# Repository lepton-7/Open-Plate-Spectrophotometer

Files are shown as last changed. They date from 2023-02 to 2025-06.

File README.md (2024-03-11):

# Open-Plate-Spectrophotometer

An open-source project to build a 96-well spectrophotometer operating at 620nm. Designed from the ground-up focusing on robust electronic design. Funded by the [think[box] Student Project Fund](https://case.edu/thinkbox/funding/student-project-fund) for the 2022-2023 academic year.

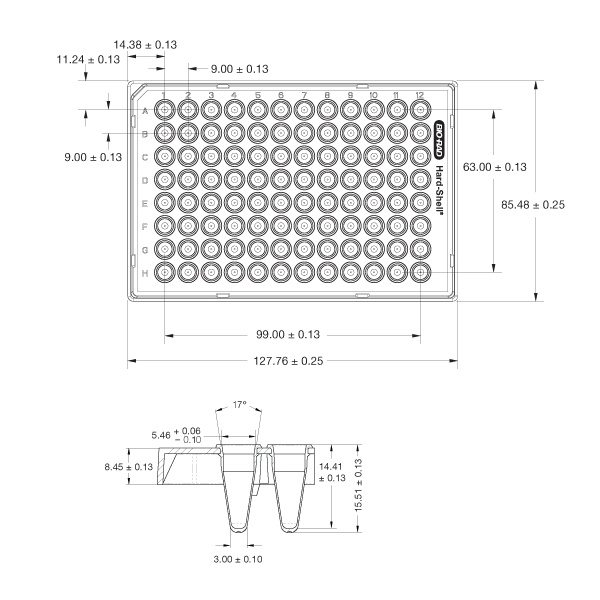
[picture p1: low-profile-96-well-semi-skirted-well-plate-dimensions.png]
plate


## Test Prototype (v0.0.2)

This project was born out of an appreciation for [Cerillo's portable microplate reader](https://cerillo.bio/stratus-2/) and the arrogant desire to open-source it by recreating what they made on my own. I designed a limited test prototype during the summer (I think sometime in July?) before the school year restarted to see what is required to realise the idea of a small form-factor, portable plate reader.

### Concept and Schematic

#### Functional block diagram

Functional block diagram

The idea is simple: control 96-element grids of LEDs and light sensors to address individual wells in a plate, convert the signal from the light sensor into something machine parsable, then finally do some ✨math✨ to get an optical density value for each well.

#### LED and detector grids

I decided to _not_ build a full 96-capable prototype. Instead, I opted to test all the relevant units I needed on a smaller scale. The result was a prototype with all 8 rows (A-H) but only two columns.

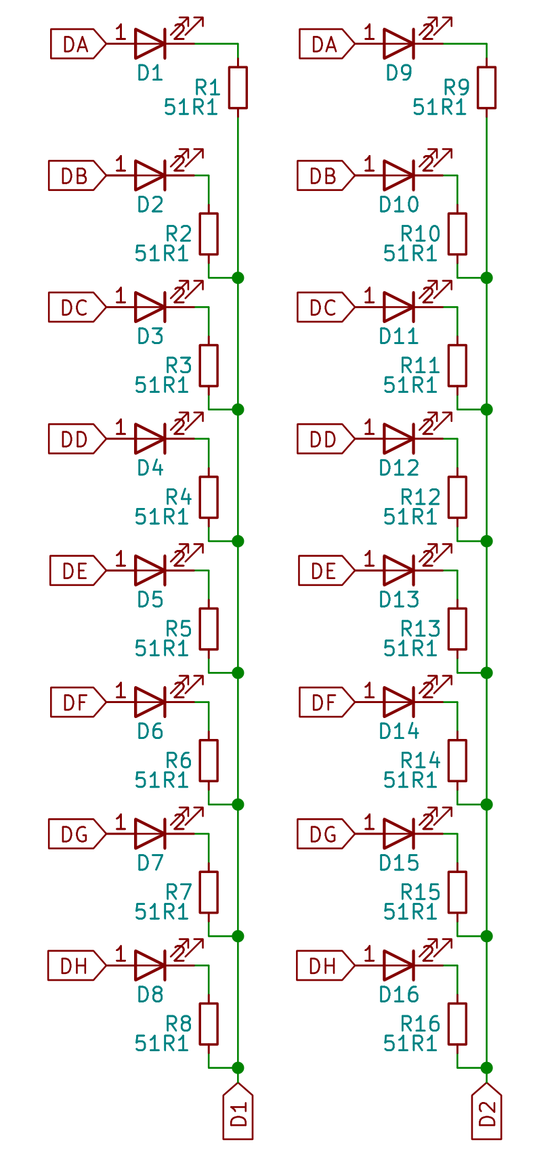
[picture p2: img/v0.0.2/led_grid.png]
led grid

Independent control of each element is easily achieved by connecting the grid high and low sides to control MOSFETs:

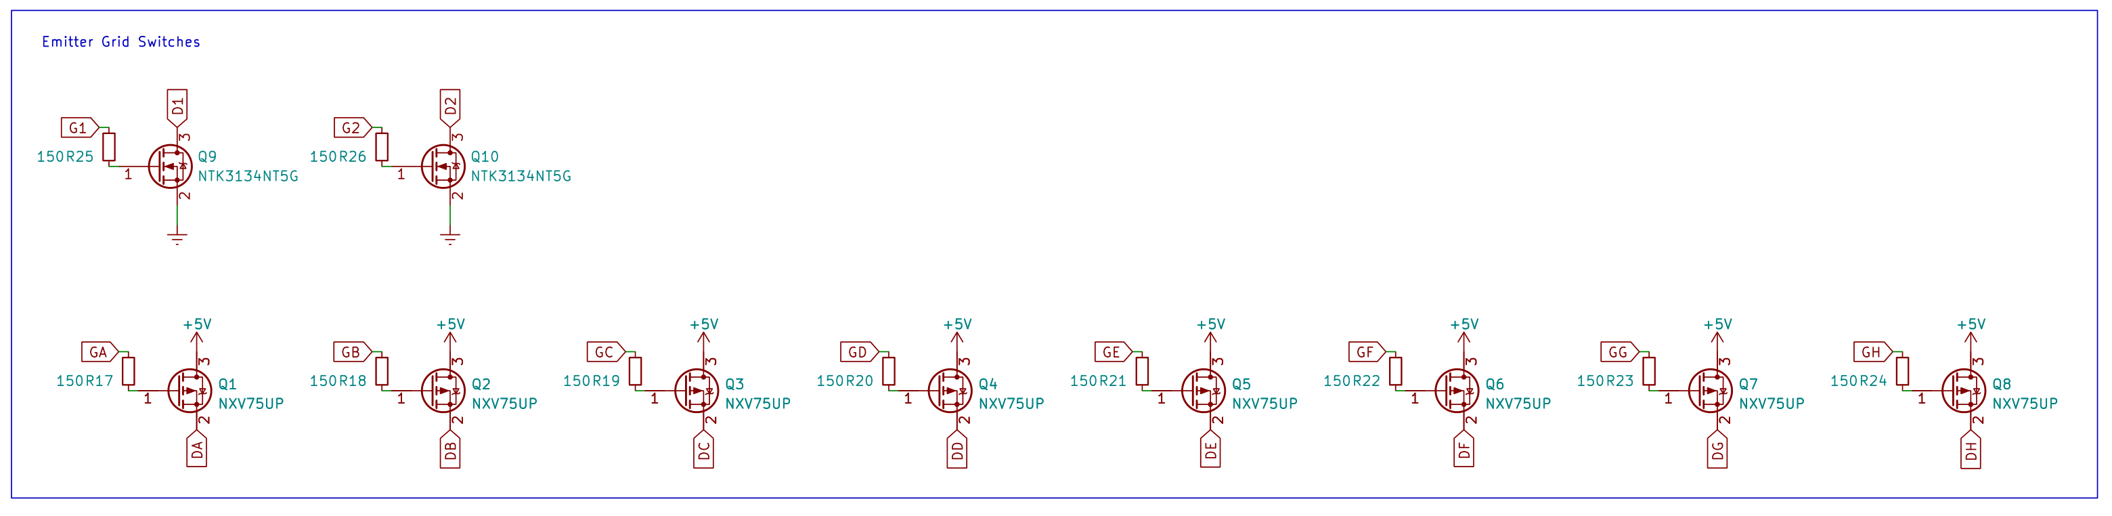
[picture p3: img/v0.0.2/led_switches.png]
led switches

Each row was connected to +5V via p-ch FETs (yes i know, they're wired incorrectly) and each column was connected to GND via n-ch FETs. Each FET gate is assigned its own pin on the MCU to independently control individual elements.

A similar idea is used for switching inputs from specific photodiode elements.

#### Detectors: photodiodes vs phototransistors

The hard bit for a device like this taking light that passes through the sample wells and converting that into a digital signal. Initially, I planned on using [phototransistors](https://www.digikey.com/en/articles/the-basics-of-photodiodes-and-phototransistors-and-how-to-apply-them) to transform a change in incident light intensity into a change in current. But these devices are pretty imprecise and do not have the best linearity. To make phototransistors work, I would have needed to do some really careful biasing -- something I did not think I needed.

The alternative was to use photodiodes. These are a bit better in the sense that they would have required a lot fewer supporting components. They also have pretty nice characteristics:

<fig>
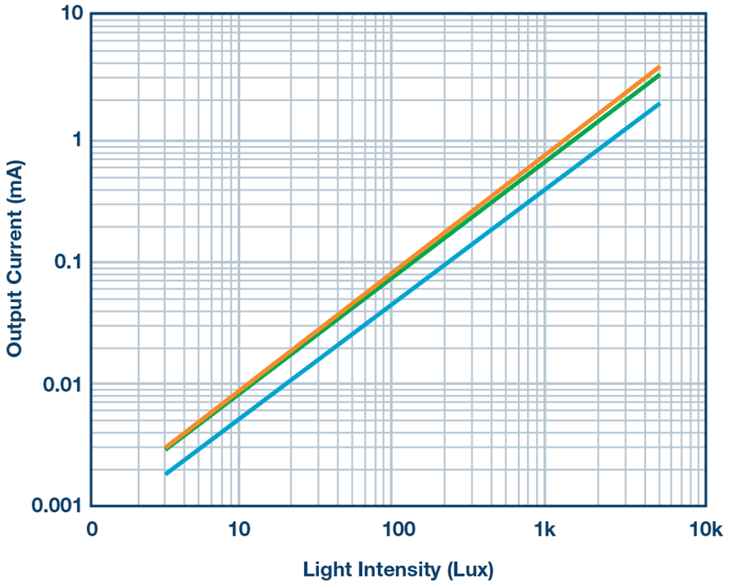
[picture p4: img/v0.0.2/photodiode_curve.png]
photodiode curve

<figcaption>Plot from Analog ADI</figcaption>
</fig>

These devices are pretty much linear in their response to incident light intensity: A 10x increase in incident intensity results in a 10x increase in reverse current.

#### Transimpedance amplifiers and ADCs

Converting current going through a photodiode into digital information is a two-step process. This is nothing new; the typical strategy is to use a transimpedance amplifier to convert transform a current signal into a voltage signal followed by an ADC that can convert the voltage signal into a digital value:

<fig>
TIA
<figcaption>TIA diagram from wikimedia commons.</figcaption>
</fig>

The transfer function is also pretty simple for a TIA:
$$ V_{out} = -I_{in}R_f $$

This is implemented as:

<fig>
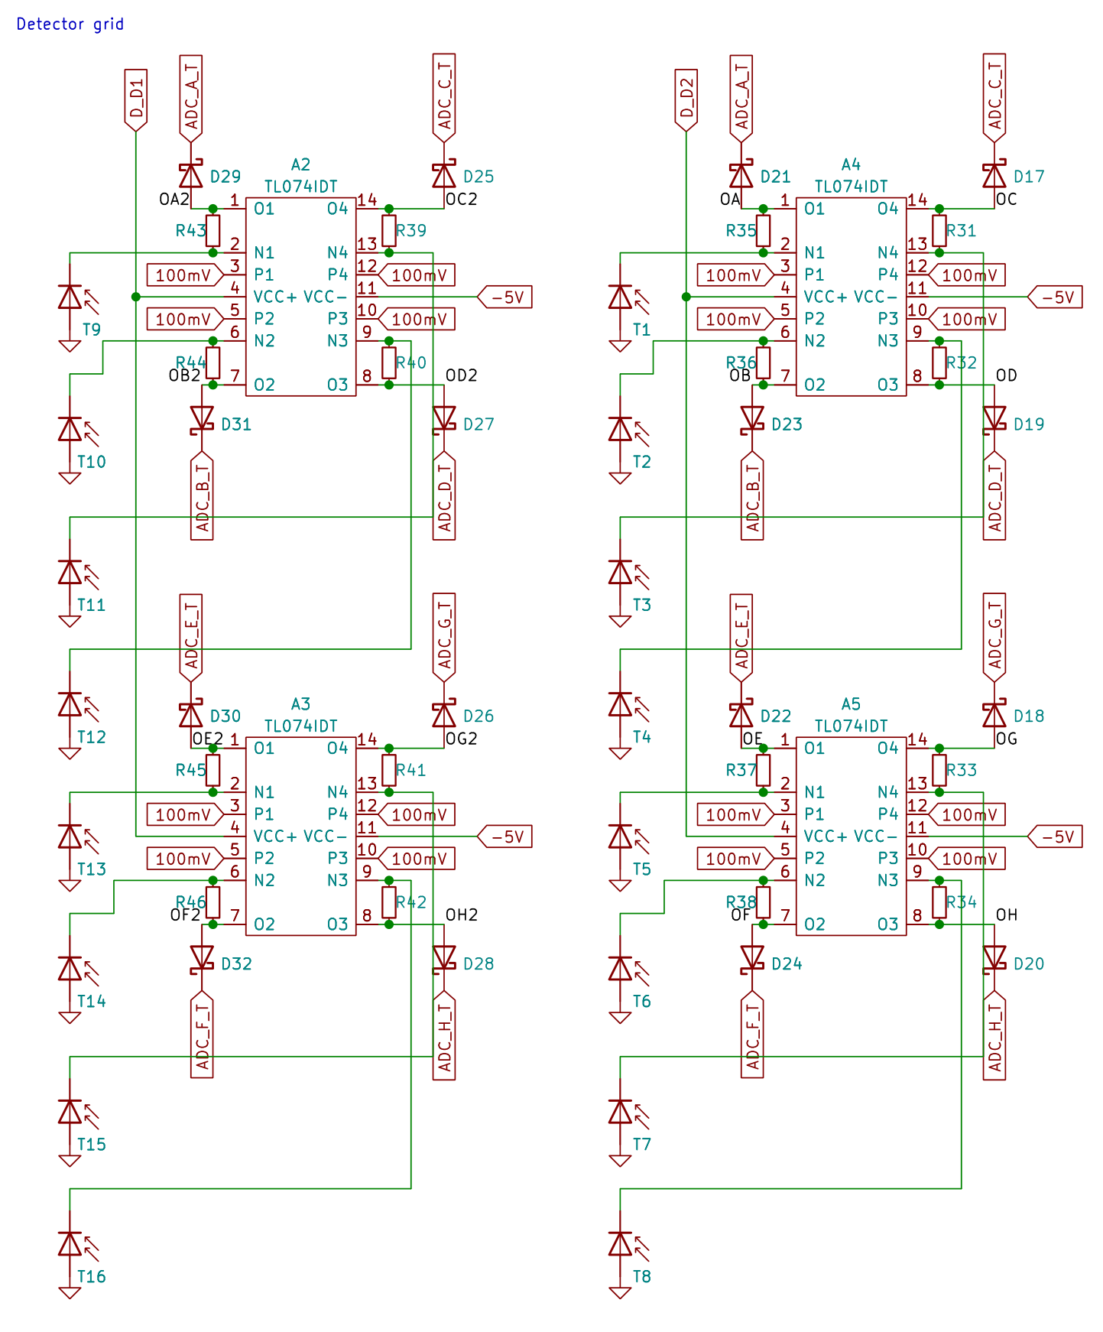
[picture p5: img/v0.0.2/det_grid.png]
photodiode grid

</fig>

The principle is the same, just compressed a little. The current source is replaced by the photodiode, mulit-channel opamps are used to save space, and $V_{out}$ passes through a standard Schottky diode before being connected to the ADC inputs.

I used an 8ch ADC to independently connect each row for pseudo-switching of the detector outputs. High-side p-ch FET switches control V<sub>cc</sub> for the TIAs.

<fig>
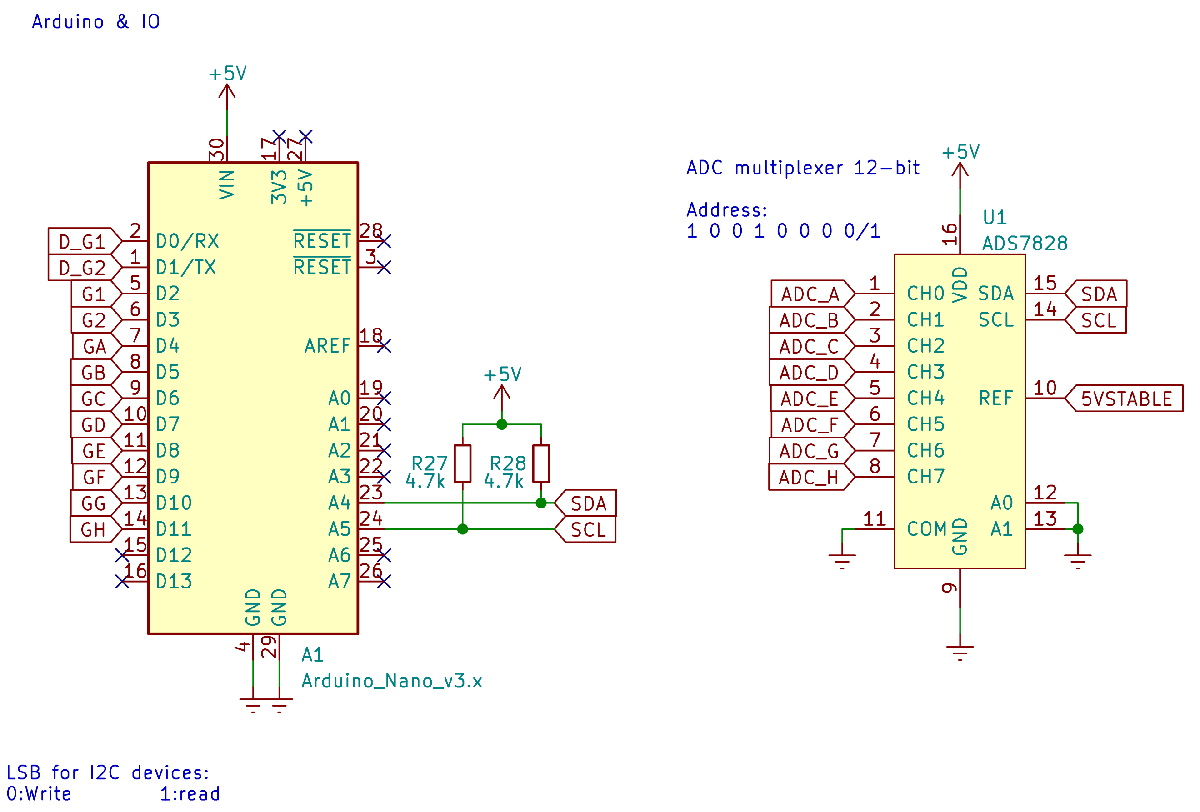
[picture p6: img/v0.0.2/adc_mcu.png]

</fig>

The 12-bit ADC converts output voltage into a digital signal referenced to a stable 5V signal generated by a voltage reference amplified by a low-noise voltage follower:

<fig>
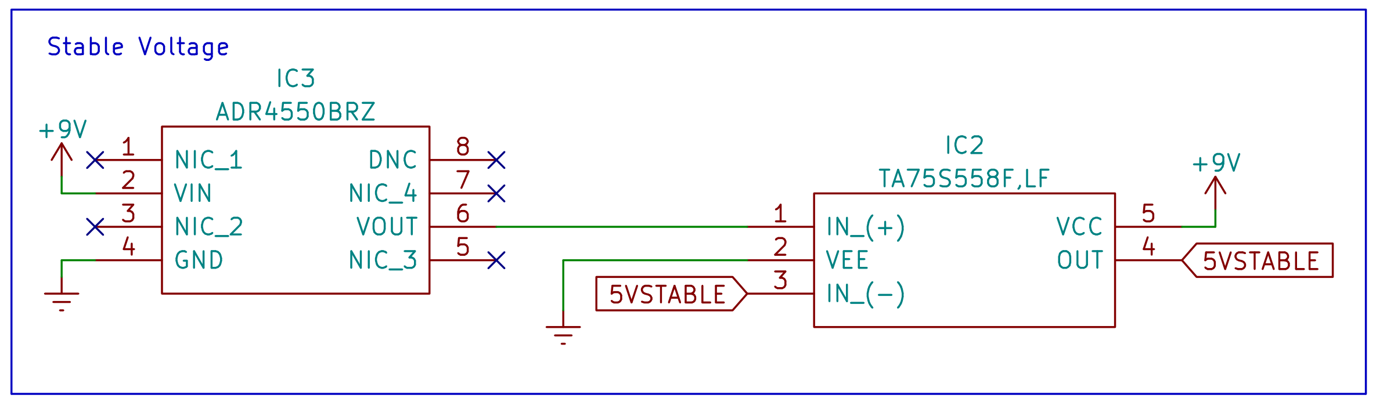
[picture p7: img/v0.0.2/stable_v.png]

</fig>

The MCU, an arduino nano, communicates with the ADC over I<sup>2</sup>C.

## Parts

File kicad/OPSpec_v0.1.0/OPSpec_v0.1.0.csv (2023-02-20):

Source: | C:\School stuff\Bagby Lab\Projects\OPSpec\kicad\OPSpec_v0.1.0\OPSpec_v0.1.0.kicad_sch
Date: | 25/11/2022 14:10
Tool: | Eeschema (6.0.5)
Generator: | C:\Program Files\KiCad\6.0\bin\scripting\plugins/bom_csv_grouped_by_value.py
Component Count: | 661
Collated Components:
Item | Qty | Reference(s) | Value | LibPart | Footprint | Datasheet | Description | Height | Manufacturer_Name | Manufacturer_Part_Number | Mouser Part Number | Mouser Price/Stock
1 | 101 | C1, C2, C3, C4, C5, C6, C7, C8, C9, C10, C11, C12, C13, C14, C15, C16, C17, C18, C19, C20, C21, C22, C23, C24, C25, C26, C27, C28, C29, C30, C31, C32, C33, C34, C35, C36, C37, C38, C39, C40, C41, C42, C43, C44, C45, C46, C47, C48, C49, C50, C51, C52, C53, C54, C55, C56, C57, C58, C59, C60, C61, C62, C63, C64, C65, C66, C67, C68, C69, C70, C71, C72, C73, C74, C75, C76, C77, C78, C79, C80, C81, C82, C83, C84, C85, C86, C87, C88, C89, C90, C91, C92, C93, C94, C95, C96, C98, C100, C105, C154, C174 | 1u | Device:C_Small | Capacitor_SMD:C_0603_1608Metric | ~
2 | 40 | C97, C99, C103, C106, C107, C108, C109, C110, C111, C112, C113, C114, C115, C116, C117, C118, C119, C120, C121, C122, C131, C132, C133, C134, C135, C136, C137, C138, C149, C151, C155, C156, C158, C161, C163, C164, C167, C169, C171, C173 | 100nF | Device:C_Small | Capacitor_SMD:C_0603_1608Metric | ~
3 | 10 | C101, C102, C104, C150, C152, C157, C160, C166, C168, C172 | 10uF | Device:C_Small | Capacitor_SMD:C_0805_2012Metric | ~
4 | 16 | C123, C124, C125, C126, C127, C128, C129, C130, C139, C140, C141, C142, C143, C144, C145, C146 | 100pF | Device:C_Small | Capacitor_SMD:C_0603_1608Metric | ~
5 | 6 | C147, C148, C159, C162, C165, C170 | 470nF | Device:C_Small | Capacitor_SMD:C_0805_2012Metric | ~
6 | 1 | C153 | 470pF | Device:C_Small | Capacitor_SMD:C_0603_1608Metric | ~
7 | 96 | D1, D2, D3, D4, D5, D6, D7, D8, D9, D10, D11, D12, D13, D14, D15, D16, D17, D18, D19, D20, D21, D22, D23, D24, D25, D26, D27, D28, D29, D30, D31, D32, D33, D34, D35, D36, D37, D38, D39, D40, D41, D42, D43, D44, D45, D46, D47, D48, D49, D50, D51, D52, D53, D54, D55, D56, D57, D58, D59, D60, D61, D62, D63, D64, D65, D66, D67, D68, D69, D70, D71, D72, D73, D74, D75, D76, D77, D78, D79, D80, D81, D82, D83, D84, D85, D86, D87, D88, D89, D90, D91, D92, D93, D94, D95, D96 | GR_JTLPS1.23-G7H4-45-1-150-R33 | LED:GR_JTLPS1.23-G7H4-45-1-150-R33 | SamacSys_Parts:GRJTLPS123G7H4451150R33 | ~ | High Power LEDs - Single Color Red DURIS E 2835 | 0.8 | OSRAM | GR JTLPS1.23-G7H4-45-1-150-R33 | 720-GRJTLPS123A1052 | https://www.mouser.co.uk/ProductDetail/OSRAM-Opto-Semiconductors/GR-JTLPS123-G7H4-45-1-150-R33?qs=T94vaHKWudSzDFhf8Pfs5w%3D%3D
8 | 8 | H1, H2, H3, H4, H5, H6, H7, H8 | MountingHole | Mechanical:MountingHole_Pad | MountingHole:MountingHole_4.3mm_M4_Pad | ~
9 | 3 | IC1, IC2, IC7 | PCA9555APW,118 | Interface_Expansion:PCA9555APW,118 | SamacSys_Parts:SOP65P640X110-24N | http://www.nxp.com/docs/en/data-sheet/PCA9555A.pdf | NXP - PCA9555APW,118 - I/O EXPANDER, 16BIT, 400KHZ, TSSOP-24 | 1.1 | NXP | PCA9555APW,118 | 771-PCA9555APW118 | https://www.mouser.co.uk/ProductDetail/NXP-Semiconductors/PCA9555APW118?qs=5C9Q4QJFsuPmpoGpn%2FKoIQ%3D%3D
10 | 1 | IC3 | MCP1801T-6002I_OT | SamacSys_Parts:MCP1801T-6002I_OT | SamacSys_Parts:SOT95P270X145-5N | https://www.mouser.in/datasheet/2/268/22051D-474537.pdf | LDO Voltage Regulators Hi PSRR 150 mA LDO Vin 10V maxVout 6.0V | 1.45 | Microchip | MCP1801T-6002I/OT | 579-MCP1801T-6002IOT | https://www.mouser.co.uk/ProductDetail/Microchip-Technology/MCP1801T-6002I-OT?qs=aE5D7Pt6ky2EwNge7jBPcQ%3D%3D
11 | 3 | IC4, IC5, IC6 | TAR5S50TE85LF | Regulator_Linear:TAR5S50TE85LF | SamacSys_Parts:SMV_1 | https://toshiba.semicon-storage.com/info/docget.jsp?did=766&prodName=TAR5S40 | LDO Voltage Regulators Point Reg SGL output 200mA 15V 5V out |  | Toshiba | TAR5S50TE85LF | 757-TAR5S50TE85LF | https://www.mouser.co.uk/ProductDetail/Toshiba/TAR5S50TE85LF?qs=lQAVKuKFhkISS%252B6HLQK7hg%3D%3D
12 | 1 | J1 | BASE_INTERFACE | :Conn_01x14_Female_1 | Connector_FFC-FPC:TE_1-1734839-4_1x14-1MP_P0.5mm_Horizontal | ~
13 | 1 | J2 | 163-179PH-EX | Connector:Barrel_Jack_Switch | Connector_BarrelJack:BarrelJack_Wuerth_6941xx301002 | ~
14 | 1 | J3 | Arduino | Connector:Conn_01x04_Male | Connector_PinHeader_2.54mm:PinHeader_1x04_P2.54mm_Vertical | ~
15 | 1 | J4 | TOP_INTERFACE | Connector:Conn_01x14_Female | Connector_FFC-FPC:TE_1-1734839-4_1x14-1MP_P0.5mm_Horizontal | ~
16 | 1 | L1 | 3.3uH | SamacSys_Parts:MAKK2016T3R3M | SamacSys_Parts:INDPM2016X100N |  | Fixed Inductors 0806 3.3uH 255mOhms +/-20% 1150A HiCur | 1 | TAIYO YUDEN | MAKK2016T3R3M | 963-MAKK2016T3R3M | https://www.mouser.co.uk/ProductDetail/Taiyo-Yuden/MAKK2016T3R3M?qs=Z6svWd%2FY2UTQY1%2FASu%252BfUw%3D%3D
17 | 8 | LA1, LA2, LA3, LA4, LA5, LA6, LA7, LA8 | MAX4206ETE+T | Amplifier_Operational:MAX4206ETE+T | SamacSys_Parts:QFN65P400X400X80-17N | https://datasheets.maximintegrated.com/en/ds/MAX4206.pdf | Logarithmic Amplifiers Precision Transimpedance Logarithmic Amplifier with Over 5 Decades of Dynamic Range | 0.8 | Maxim Integrated | MAX4206ETE+T | 700-MAX4206ETE+T | https://www.mouser.co.uk/ProductDetail/Maxim-Integrated/MAX4206ETE%2bT?qs=1eQvB6Dk1vihFrrDtkPdrA%3D%3D
18 | 12 | Q1, Q2, Q3, Q4, Q5, Q6, Q7, Q8, Q9, Q10, Q11, Q12 | NTK3134NT5G | Device:Q_NMOS_GSD | SamacSys_Parts:NTK3134NT5G | https://www.onsemi.com/pdf/datasheet/ntk3134n-d.pdf | N-Channel 20 V 750mA (Ta) 310mW (Ta) Surface Mount SOT-723 | 0.55 | onsemi | NTK3134NT5G | 863-NTK3134NT5G | https://www.mouser.co.uk/ProductDetail/onsemi/NTK3134NT5G?qs=g97OBWmz8%2FWdltr4eSy1YA%3D%3D
19 | 20 | Q13, Q14, Q15, Q16, Q17, Q18, Q19, Q20, Q21, Q22, Q23, Q24, Q25, Q26, Q27, Q28, Q29, Q30, Q31, Q32 | NXV75UP | Device:Q_PMOS_GSD | Package_TO_SOT_SMD:SOT-23 | ~
20 | 6 | Q33, Q34, Q35, Q36, Q37, Q38 | 2SCR502UBTL | Transistor_BJT:2SCR502UBTL | SamacSys_Parts:SOTFL65P210X105-3N | https://componentsearchengine.com/Datasheets/1/2SCR502UBTL.pdf | Signal Transistor NPN 30V 500mA UMT3F | 1.05 | ROHM Semiconductor | 2SCR502UBTL | 755-2SCR502UBTL | https://www.mouser.com/Search/Refine.aspx?Keyword=755-2SCR502UBTL
21 | 96 | R1, R2, R3, R4, R5, R6, R7, R8, R9, R10, R11, R12, R13, R14, R15, R16, R17, R18, R19, R20, R21, R22, R23, R24, R25, R26, R27, R28, R29, R30, R31, R32, R33, R34, R35, R36, R37, R38, R39, R40, R41, R42, R43, R44, R45, R46, R47, R48, R49, R50, R51, R52, R53, R54, R55, R56, R57, R58, R59, R60, R61, R62, R63, R64, R65, R66, R67, R68, R69, R70, R71, R72, R73, R74, R75, R76, R77, R78, R79, R80, R81, R82, R83, R84, R85, R86, R87, R88, R89, R90, R91, R92, R93, R94, R95, R96 | 51R1 | Device:R_Small | Resistor_SMD:R_0603_1608Metric | ~
22 | 32 | R97, R99, R101, R103, R105, R107, R109, R111, R113, R115, R117, R119, R129, R130, R131, R132, R133, R134, R135, R136, R142, R144, R146, R148, R150, R152, R154, R156, R158, R160, R162, R164 | 100k | Device:R_Small | Resistor_SMD:R_0603_1608Metric | ~
23 | 32 | R98, R100, R102, R104, R106, R108, R110, R112, R114, R116, R118, R120, R121, R122, R123, R124, R125, R126, R127, R128, R141, R143, R145, R147, R149, R151, R153, R155, R157, R159, R161, R163 | 150 | Device:R_Small | Resistor_SMD:R_0603_1608Metric | ~
24 | 27 | R137, R138, R173, R174, R175, R176, R177, R178, R179, R180, R211, R212, R213, R214, R215, R216, R217, R218, R219, R220, R221, R222, R223, R224, R225, R226, R227 | 10k | Device:R_Small | Resistor_SMD:R_0603_1608Metric | ~
25 | 2 | R139, R140 | 4.7k | Device:R_Small | Resistor_SMD:R_0603_1608Metric | ~
26 | 8 | R165, R166, R167, R168, R169, R170, R171, R172 | 38k3 | Device:R_Small | Resistor_SMD:R_0603_1608Metric | ~
27 | 8 | R181, R182, R183, R184, R185, R186, R187, R188 | 499k | Device:R_Small | Resistor_SMD:R_0603_1608Metric | ~
28 | 16 | R189, R190, R191, R192, R193, R194, R195, R196, R197, R198, R199, R200, R201, R202, R203, R204 | 100 | Device:R_Small | Resistor_SMD:R_0603_1608Metric | ~
29 | 6 | R205, R206, R207, R208, R209, R210 | 511 | Device:R_Small | Resistor_SMD:R_0603_1608Metric | ~
30 | 96 | T1, T2, T3, T4, T5, T6, T7, T8, T9, T10, T11, T12, T13, T14, T15, T16, T17, T18, T19, T20, T21, T22, T23, T24, T25, T26, T27, T28, T29, T30, T31, T32, T33, T34, T35, T36, T37, T38, T39, T40, T41, T42, T43, T44, T45, T46, T47, T48, T49, T50, T51, T52, T53, T54, T55, T56, T57, T58, T59, T60, T61, T62, T63, T64, T65, T66, T67, T68, T69, T70, T71, T72, T73, T74, T75, T76, T77, T78, T79, T80, T81, T82, T83, T84, T85, T86, T87, T88, T89, T90, T91, T92, T93, T94, T95, T96 | S16392-01CT | Device:D_Photo | Diode_SMD:S16392-01CT | ~
31 | 1 | U1 | AP63205WU | Regulator_Switching:AP63205WU | Package_TO_SOT_SMD:TSOT-23-6 | https://www.diodes.com/assets/Datasheets/AP63200-AP63201-AP63203-AP63205.pdf
32 | 1 | U2 | ADS7828 | Analog_ADC:ADS7828 | Package_SO:TSSOP-16_4.4x5mm_P0.65mm | http://www.ti.com/lit/ds/symlink/ads7828.pdf
Individual Components:
Item | Qty | Reference(s) | Value | LibPart | Footprint | Datasheet | Description | Height | Manufacturer_Name | Manufacturer_Part_Number | Mouser Part Number | Mouser Price/Stock
 |  | C1 | 1u | Device:C_Small | Capacitor_SMD:C_0603_1608Metric | ~
 |  | C2 | 1u | Device:C_Small | Capacitor_SMD:C_0603_1608Metric | ~
 |  | C3 | 1u | Device:C_Small | Capacitor_SMD:C_0603_1608Metric | ~
 |  | C4 | 1u | Device:C_Small | Capacitor_SMD:C_0603_1608Metric | ~
 |  | C5 | 1u | Device:C_Small | Capacitor_SMD:C_0603_1608Metric | ~
 |  | C6 | 1u | Device:C_Small | Capacitor_SMD:C_0603_1608Metric | ~
 |  | C7 | 1u | Device:C_Small | Capacitor_SMD:C_0603_1608Metric | ~
 |  | C8 | 1u | Device:C_Small | Capacitor_SMD:C_0603_1608Metric | ~
 |  | C9 | 1u | Device:C_Small | Capacitor_SMD:C_0603_1608Metric | ~
 |  | C10 | 1u | Device:C_Small | Capacitor_SMD:C_0603_1608Metric | ~
 |  | C11 | 1u | Device:C_Small | Capacitor_SMD:C_0603_1608Metric | ~
 |  | C12 | 1u | Device:C_Small | Capacitor_SMD:C_0603_1608Metric | ~
 |  | C13 | 1u | Device:C_Small | Capacitor_SMD:C_0603_1608Metric | ~
 |  | C14 | 1u | Device:C_Small | Capacitor_SMD:C_0603_1608Metric | ~
 |  | C15 | 1u | Device:C_Small | Capacitor_SMD:C_0603_1608Metric | ~
 |  | C16 | 1u | Device:C_Small | Capacitor_SMD:C_0603_1608Metric | ~
 |  | C17 | 1u | Device:C_Small | Capacitor_SMD:C_0603_1608Metric | ~
 |  | C18 | 1u | Device:C_Small | Capacitor_SMD:C_0603_1608Metric | ~
 |  | C19 | 1u | Device:C_Small | Capacitor_SMD:C_0603_1608Metric | ~
 |  | C20 | 1u | Device:C_Small | Capacitor_SMD:C_0603_1608Metric | ~
 |  | C21 | 1u | Device:C_Small | Capacitor_SMD:C_0603_1608Metric | ~
 |  | C22 | 1u | Device:C_Small | Capacitor_SMD:C_0603_1608Metric | ~
 |  | C23 | 1u | Device:C_Small | Capacitor_SMD:C_0603_1608Metric | ~
 |  | C24 | 1u | Device:C_Small | Capacitor_SMD:C_0603_1608Metric | ~
 |  | C25 | 1u | Device:C_Small | Capacitor_SMD:C_0603_1608Metric | ~
 |  | C26 | 1u | Device:C_Small | Capacitor_SMD:C_0603_1608Metric | ~
 |  | C27 | 1u | Device:C_Small | Capacitor_SMD:C_0603_1608Metric | ~
 |  | C28 | 1u | Device:C_Small | Capacitor_SMD:C_0603_1608Metric | ~
 |  | C29 | 1u | Device:C_Small | Capacitor_SMD:C_0603_1608Metric | ~
 |  | C30 | 1u | Device:C_Small | Capacitor_SMD:C_0603_1608Metric | ~
 |  | C31 | 1u | Device:C_Small | Capacitor_SMD:C_0603_1608Metric | ~
 |  | C32 | 1u | Device:C_Small | Capacitor_SMD:C_0603_1608Metric | ~
 |  | C33 | 1u | Device:C_Small | Capacitor_SMD:C_0603_1608Metric | ~
 |  | C34 | 1u | Device:C_Small | Capacitor_SMD:C_0603_1608Metric | ~
 |  | C35 | 1u | Device:C_Small | Capacitor_SMD:C_0603_1608Metric | ~
 |  | C36 | 1u | Device:C_Small | Capacitor_SMD:C_0603_1608Metric | ~
 |  | C37 | 1u | Device:C_Small | Capacitor_SMD:C_0603_1608Metric | ~
 |  | C38 | 1u | Device:C_Small | Capacitor_SMD:C_0603_1608Metric | ~
 |  | C39 | 1u | Device:C_Small | Capacitor_SMD:C_0603_1608Metric | ~
 |  | C40 | 1u | Device:C_Small | Capacitor_SMD:C_0603_1608Metric | ~
 |  | C41 | 1u | Device:C_Small | Capacitor_SMD:C_0603_1608Metric | ~
 |  | C42 | 1u | Device:C_Small | Capacitor_SMD:C_0603_1608Metric | ~
 |  | C43 | 1u | Device:C_Small | Capacitor_SMD:C_0603_1608Metric | ~
 |  | C44 | 1u | Device:C_Small | Capacitor_SMD:C_0603_1608Metric | ~
 |  | C45 | 1u | Device:C_Small | Capacitor_SMD:C_0603_1608Metric | ~
 |  | C46 | 1u | Device:C_Small | Capacitor_SMD:C_0603_1608Metric | ~
 |  | C47 | 1u | Device:C_Small | Capacitor_SMD:C_0603_1608Metric | ~
 |  | C48 | 1u | Device:C_Small | Capacitor_SMD:C_0603_1608Metric | ~
 |  | C49 | 1u | Device:C_Small | Capacitor_SMD:C_0603_1608Metric | ~
 |  | C50 | 1u | Device:C_Small | Capacitor_SMD:C_0603_1608Metric | ~
 |  | C51 | 1u | Device:C_Small | Capacitor_SMD:C_0603_1608Metric | ~
 |  | C52 | 1u | Device:C_Small | Capacitor_SMD:C_0603_1608Metric | ~
 |  | C53 | 1u | Device:C_Small | Capacitor_SMD:C_0603_1608Metric | ~
 |  | C54 | 1u | Device:C_Small | Capacitor_SMD:C_0603_1608Metric | ~
 |  | C55 | 1u | Device:C_Small | Capacitor_SMD:C_0603_1608Metric | ~
 |  | C56 | 1u | Device:C_Small | Capacitor_SMD:C_0603_1608Metric | ~
 |  | C57 | 1u | Device:C_Small | Capacitor_SMD:C_0603_1608Metric | ~
 |  | C58 | 1u | Device:C_Small | Capacitor_SMD:C_0603_1608Metric | ~
 |  | C59 | 1u | Device:C_Small | Capacitor_SMD:C_0603_1608Metric | ~
 |  | C60 | 1u | Device:C_Small | Capacitor_SMD:C_0603_1608Metric | ~
 |  | C61 | 1u | Device:C_Small | Capacitor_SMD:C_0603_1608Metric | ~
 |  | C62 | 1u | Device:C_Small | Capacitor_SMD:C_0603_1608Metric | ~
 |  | C63 | 1u | Device:C_Small | Capacitor_SMD:C_0603_1608Metric | ~
 |  | C64 | 1u | Device:C_Small | Capacitor_SMD:C_0603_1608Metric | ~
 |  | C65 | 1u | Device:C_Small | Capacitor_SMD:C_0603_1608Metric | ~
 |  | C66 | 1u | Device:C_Small | Capacitor_SMD:C_0603_1608Metric | ~
 |  | C67 | 1u | Device:C_Small | Capacitor_SMD:C_0603_1608Metric | ~
 |  | C68 | 1u | Device:C_Small | Capacitor_SMD:C_0603_1608Metric | ~
 |  | C69 | 1u | Device:C_Small | Capacitor_SMD:C_0603_1608Metric | ~
 |  | C70 | 1u | Device:C_Small | Capacitor_SMD:C_0603_1608Metric | ~
 |  | C71 | 1u | Device:C_Small | Capacitor_SMD:C_0603_1608Metric | ~
 |  | C72 | 1u | Device:C_Small | Capacitor_SMD:C_0603_1608Metric | ~
 |  | C73 | 1u | Device:C_Small | Capacitor_SMD:C_0603_1608Metric | ~
 |  | C74 | 1u | Device:C_Small | Capacitor_SMD:C_0603_1608Metric | ~
 |  | C75 | 1u | Device:C_Small | Capacitor_SMD:C_0603_1608Metric | ~
 |  | C76 | 1u | Device:C_Small | Capacitor_SMD:C_0603_1608Metric | ~
 |  | C77 | 1u | Device:C_Small | Capacitor_SMD:C_0603_1608Metric | ~
 |  | C78 | 1u | Device:C_Small | Capacitor_SMD:C_0603_1608Metric | ~
 |  | C79 | 1u | Device:C_Small | Capacitor_SMD:C_0603_1608Metric | ~
 |  | C80 | 1u | Device:C_Small | Capacitor_SMD:C_0603_1608Metric | ~
 |  | C81 | 1u | Device:C_Small | Capacitor_SMD:C_0603_1608Metric | ~
 |  | C82 | 1u | Device:C_Small | Capacitor_SMD:C_0603_1608Metric | ~
 |  | C83 | 1u | Device:C_Small | Capacitor_SMD:C_0603_1608Metric | ~
 |  | C84 | 1u | Device:C_Small | Capacitor_SMD:C_0603_1608Metric | ~
 |  | C85 | 1u | Device:C_Small | Capacitor_SMD:C_0603_1608Metric | ~
 |  | C86 | 1u | Device:C_Small | Capacitor_SMD:C_0603_1608Metric | ~
 |  | C87 | 1u | Device:C_Small | Capacitor_SMD:C_0603_1608Metric | ~
 |  | C88 | 1u | Device:C_Small | Capacitor_SMD:C_0603_1608Metric | ~
 |  | C89 | 1u | Device:C_Small | Capacitor_SMD:C_0603_1608Metric | ~
 |  | C90 | 1u | Device:C_Small | Capacitor_SMD:C_0603_1608Metric | ~
 |  | C91 | 1u | Device:C_Small | Capacitor_SMD:C_0603_1608Metric | ~
 |  | C92 | 1u | Device:C_Small | Capacitor_SMD:C_0603_1608Metric | ~
 |  | C93 | 1u | Device:C_Small | Capacitor_SMD:C_0603_1608Metric | ~
 |  | C94 | 1u | Device:C_Small | Capacitor_SMD:C_0603_1608Metric | ~
 |  | C95 | 1u | Device:C_Small | Capacitor_SMD:C_0603_1608Metric | ~
 |  | C96 | 1u | Device:C_Small | Capacitor_SMD:C_0603_1608Metric | ~
 |  | C97 | 100nF | Device:C_Small | Capacitor_SMD:C_0603_1608Metric | ~
 |  | C98 | 1u | Device:C_Small | Capacitor_SMD:C_0603_1608Metric | ~
 |  | C99 | 100nF | Device:C_Small | Capacitor_SMD:C_0603_1608Metric | ~
 |  | C100 | 1u | Device:C_Small | Capacitor_SMD:C_0603_1608Metric | ~
 |  | C101 | 10uF | Device:C_Small | Capacitor_SMD:C_0805_2012Metric | ~
 |  | C102 | 10uF | Device:C_Small | Capacitor_SMD:C_0805_2012Metric | ~
 |  | C103 | 100nF | Device:C_Small | Capacitor_SMD:C_0603_1608Metric | ~
 |  | C104 | 10uF | Device:C_Small | Capacitor_SMD:C_0805_2012Metric | ~
 |  | C105 | 1u | Device:C_Small | Capacitor_SMD:C_0603_1608Metric | ~
 |  | C106 | 100nF | Device:C_Small | Capacitor_SMD:C_0603_1608Metric | ~
 |  | C107 | 100nF | Device:C_Small | Capacitor_SMD:C_0603_1608Metric | ~
 |  | C108 | 100nF | Device:C_Small | Capacitor_SMD:C_0603_1608Metric | ~
 |  | C109 | 100nF | Device:C_Small | Capacitor_SMD:C_0603_1608Metric | ~
 |  | C110 | 100nF | Device:C_Small | Capacitor_SMD:C_0603_1608Metric | ~
 |  | C111 | 100nF | Device:C_Small | Capacitor_SMD:C_0603_1608Metric | ~
 |  | C112 | 100nF | Device:C_Small | Capacitor_SMD:C_0603_1608Metric | ~
 |  | C113 | 100nF | Device:C_Small | Capacitor_SMD:C_0603_1608Metric | ~
 |  | C114 | 100nF | Device:C_Small | Capacitor_SMD:C_0603_1608Metric | ~
 |  | C115 | 100nF | Device:C_Small | Capacitor_SMD:C_0603_1608Metric | ~
 |  | C116 | 100nF | Device:C_Small | Capacitor_SMD:C_0603_1608Metric | ~
 |  | C117 | 100nF | Device:C_Small | Capacitor_SMD:C_0603_1608Metric | ~
 |  | C118 | 100nF | Device:C_Small | Capacitor_SMD:C_0603_1608Metric | ~
 |  | C119 | 100nF | Device:C_Small | Capacitor_SMD:C_0603_1608Metric | ~
 |  | C120 | 100nF | Device:C_Small | Capacitor_SMD:C_0603_1608Metric | ~
 |  | C121 | 100nF | Device:C_Small | Capacitor_SMD:C_0603_1608Metric | ~
 |  | C122 | 100nF | Device:C_Small | Capacitor_SMD:C_0603_1608Metric | ~
 |  | C123 | 100pF | Device:C_Small | Capacitor_SMD:C_0603_1608Metric | ~
 |  | C124 | 100pF | Device:C_Small | Capacitor_SMD:C_0603_1608Metric | ~
 |  | C125 | 100pF | Device:C_Small | Capacitor_SMD:C_0603_1608Metric | ~
 |  | C126 | 100pF | Device:C_Small | Capacitor_SMD:C_0603_1608Metric | ~
 |  | C127 | 100pF | Device:C_Small | Capacitor_SMD:C_0603_1608Metric | ~
 |  | C128 | 100pF | Device:C_Small | Capacitor_SMD:C_0603_1608Metric | ~
 |  | C129 | 100pF | Device:C_Small | Capacitor_SMD:C_0603_1608Metric | ~
 |  | C130 | 100pF | Device:C_Small | Capacitor_SMD:C_0603_1608Metric | ~
 |  | C131 | 100nF | Device:C_Small | Capacitor_SMD:C_0603_1608Metric | ~
 |  | C132 | 100nF | Device:C_Small | Capacitor_SMD:C_0603_1608Metric | ~
 |  | C133 | 100nF | Device:C_Small | Capacitor_SMD:C_0603_1608Metric | ~
 |  | C134 | 100nF | Device:C_Small | Capacitor_SMD:C_0603_1608Metric | ~
 |  | C135 | 100nF | Device:C_Small | Capacitor_SMD:C_0603_1608Metric | ~
 |  | C136 | 100nF | Device:C_Small | Capacitor_SMD:C_0603_1608Metric | ~
 |  | C137 | 100nF | Device:C_Small | Capacitor_SMD:C_0603_1608Metric | ~
 |  | C138 | 100nF | Device:C_Small | Capacitor_SMD:C_0603_1608Metric | ~
 |  | C139 | 100pF | Device:C_Small | Capacitor_SMD:C_0603_1608Metric | ~
 |  | C140 | 100pF | Device:C_Small | Capacitor_SMD:C_0603_1608Metric | ~
 |  | C141 | 100pF | Device:C_Small | Capacitor_SMD:C_0603_1608Metric | ~
 |  | C142 | 100pF | Device:C_Small | Capacitor_SMD:C_0603_1608Metric | ~
 |  | C143 | 100pF | Device:C_Small | Capacitor_SMD:C_0603_1608Metric | ~
 |  | C144 | 100pF | Device:C_Small | Capacitor_SMD:C_0603_1608Metric | ~
 |  | C145 | 100pF | Device:C_Small | Capacitor_SMD:C_0603_1608Metric | ~
 |  | C146 | 100pF | Device:C_Small | Capacitor_SMD:C_0603_1608Metric | ~
 |  | C147 | 470nF | Device:C_Small | Capacitor_SMD:C_0805_2012Metric | ~
 |  | C148 | 470nF | Device:C_Small | Capacitor_SMD:C_0805_2012Metric | ~
 |  | C149 | 100nF | Device:C_Small | Capacitor_SMD:C_0603_1608Metric | ~
 |  | C150 | 10uF | Device:C_Small | Capacitor_SMD:C_0805_2012Metric | ~
 |  | C151 | 100nF | Device:C_Small | Capacitor_SMD:C_0603_1608Metric | ~
 |  | C152 | 10uF | Device:C_Small | Capacitor_SMD:C_0805_2012Metric | ~
 |  | C153 | 470pF | Device:C_Small | Capacitor_SMD:C_0603_1608Metric | ~
 |  | C154 | 1u | Device:C_Small | Capacitor_SMD:C_0603_1608Metric | ~
 |  | C155 | 100nF | Device:C_Small | Capacitor_SMD:C_0603_1608Metric | ~
 |  | C156 | 100nF | Device:C_Small | Capacitor_SMD:C_0603_1608Metric | ~
 |  | C157 | 10uF | Device:C_Small | Capacitor_SMD:C_0805_2012Metric | ~
 |  | C158 | 100nF | Device:C_Small | Capacitor_SMD:C_0603_1608Metric | ~
 |  | C159 | 470nF | Device:C_Small | Capacitor_SMD:C_0805_2012Metric | ~
 |  | C160 | 10uF | Device:C_Small | Capacitor_SMD:C_0805_2012Metric | ~
 |  | C161 | 100nF | Device:C_Small | Capacitor_SMD:C_0603_1608Metric | ~
 |  | C162 | 470nF | Device:C_Small | Capacitor_SMD:C_0805_2012Metric | ~
 |  | C163 | 100nF | Device:C_Small | Capacitor_SMD:C_0603_1608Metric | ~
 |  | C164 | 100nF | Device:C_Small | Capacitor_SMD:C_0603_1608Metric | ~
 |  | C165 | 470nF | Device:C_Small | Capacitor_SMD:C_0805_2012Metric | ~
 |  | C166 | 10uF | Device:C_Small | Capacitor_SMD:C_0805_2012Metric | ~
 |  | C167 | 100nF | Device:C_Small | Capacitor_SMD:C_0603_1608Metric | ~
 |  | C168 | 10uF | Device:C_Small | Capacitor_SMD:C_0805_2012Metric | ~
 |  | C169 | 100nF | Device:C_Small | Capacitor_SMD:C_0603_1608Metric | ~
 |  | C170 | 470nF | Device:C_Small | Capacitor_SMD:C_0805_2012Metric | ~
 |  | C171 | 100nF | Device:C_Small | Capacitor_SMD:C_0603_1608Metric | ~
 |  | C172 | 10uF | Device:C_Small | Capacitor_SMD:C_0805_2012Metric | ~
 |  | C173 | 100nF | Device:C_Small | Capacitor_SMD:C_0603_1608Metric | ~
 |  | C174 | 1u | Device:C_Small | Capacitor_SMD:C_0603_1608Metric | ~
 |  | D1 | GR_JTLPS1.23-G7H4-45-1-150-R33 | LED:GR_JTLPS1.23-G7H4-45-1-150-R33 | SamacSys_Parts:GRJTLPS123G7H4451150R33 | ~ | High Power LEDs - Single Color Red DURIS E 2835 | 0.8 | OSRAM | GR JTLPS1.23-G7H4-45-1-150-R33 | 720-GRJTLPS123A1052 | https://www.mouser.co.uk/ProductDetail/OSRAM-Opto-Semiconductors/GR-JTLPS123-G7H4-45-1-150-R33?qs=T94vaHKWudSzDFhf8Pfs5w%3D%3D
 |  | D2 | GR_JTLPS1.23-G7H4-45-1-150-R33 | LED:GR_JTLPS1.23-G7H4-45-1-150-R33 | SamacSys_Parts:GRJTLPS123G7H4451150R33 | ~ | High Power LEDs - Single Color Red DURIS E 2835 | 0.8 | OSRAM | GR JTLPS1.23-G7H4-45-1-150-R33 | 720-GRJTLPS123A1052 | https://www.mouser.co.uk/ProductDetail/OSRAM-Opto-Semiconductors/GR-JTLPS123-G7H4-45-1-150-R33?qs=T94vaHKWudSzDFhf8Pfs5w%3D%3D
 |  | D3 | GR_JTLPS1.23-G7H4-45-1-150-R33 | LED:GR_JTLPS1.23-G7H4-45-1-150-R33 | SamacSys_Parts:GRJTLPS123G7H4451150R33 | ~ | High Power LEDs - Single Color Red DURIS E 2835 | 0.8 | OSRAM | GR JTLPS1.23-G7H4-45-1-150-R33 | 720-GRJTLPS123A1052 | https://www.mouser.co.uk/ProductDetail/OSRAM-Opto-Semiconductors/GR-JTLPS123-G7H4-45-1-150-R33?qs=T94vaHKWudSzDFhf8Pfs5w%3D%3D
 |  | D4 | GR_JTLPS1.23-G7H4-45-1-150-R33 | LED:GR_JTLPS1.23-G7H4-45-1-150-R33 | SamacSys_Parts:GRJTLPS123G7H4451150R33 | ~ | High Power LEDs - Single Color Red DURIS E 2835 | 0.8 | OSRAM | GR JTLPS1.23-G7H4-45-1-150-R33 | 720-GRJTLPS123A1052 | https://www.mouser.co.uk/ProductDetail/OSRAM-Opto-Semiconductors/GR-JTLPS123-G7H4-45-1-150-R33?qs=T94vaHKWudSzDFhf8Pfs5w%3D%3D
 |  | D5 | GR_JTLPS1.23-G7H4-45-1-150-R33 | LED:GR_JTLPS1.23-G7H4-45-1-150-R33 | SamacSys_Parts:GRJTLPS123G7H4451150R33 | ~ | High Power LEDs - Single Color Red DURIS E 2835 | 0.8 | OSRAM | GR JTLPS1.23-G7H4-45-1-150-R33 | 720-GRJTLPS123A1052 | https://www.mouser.co.uk/ProductDetail/OSRAM-Opto-Semiconductors/GR-JTLPS123-G7H4-45-1-150-R33?qs=T94vaHKWudSzDFhf8Pfs5w%3D%3D
 |  | D6 | GR_JTLPS1.23-G7H4-45-1-150-R33 | LED:GR_JTLPS1.23-G7H4-45-1-150-R33 | SamacSys_Parts:GRJTLPS123G7H4451150R33 | ~ | High Power LEDs - Single Color Red DURIS E 2835 | 0.8 | OSRAM | GR JTLPS1.23-G7H4-45-1-150-R33 | 720-GRJTLPS123A1052 | https://www.mouser.co.uk/ProductDetail/OSRAM-Opto-Semiconductors/GR-JTLPS123-G7H4-45-1-150-R33?qs=T94vaHKWudSzDFhf8Pfs5w%3D%3D
 |  | D7 | GR_JTLPS1.23-G7H4-45-1-150-R33 | LED:GR_JTLPS1.23-G7H4-45-1-150-R33 | SamacSys_Parts:GRJTLPS123G7H4451150R33 | ~ | High Power LEDs - Single Color Red DURIS E 2835 | 0.8 | OSRAM | GR JTLPS1.23-G7H4-45-1-150-R33 | 720-GRJTLPS123A1052 | https://www.mouser.co.uk/ProductDetail/OSRAM-Opto-Semiconductors/GR-JTLPS123-G7H4-45-1-150-R33?qs=T94vaHKWudSzDFhf8Pfs5w%3D%3D
 |  | D8 | GR_JTLPS1.23-G7H4-45-1-150-R33 | LED:GR_JTLPS1.23-G7H4-45-1-150-R33 | SamacSys_Parts:GRJTLPS123G7H4451150R33 | ~ | High Power LEDs - Single Color Red DURIS E 2835 | 0.8 | OSRAM | GR JTLPS1.23-G7H4-45-1-150-R33 | 720-GRJTLPS123A1052 | https://www.mouser.co.uk/ProductDetail/OSRAM-Opto-Semiconductors/GR-JTLPS123-G7H4-45-1-150-R33?qs=T94vaHKWudSzDFhf8Pfs5w%3D%3D
 |  | D9 | GR_JTLPS1.23-G7H4-45-1-150-R33 | LED:GR_JTLPS1.23-G7H4-45-1-150-R33 | SamacSys_Parts:GRJTLPS123G7H4451150R33 | ~ | High Power LEDs - Single Color Red DURIS E 2835 | 0.8 | OSRAM | GR JTLPS1.23-G7H4-45-1-150-R33 | 720-GRJTLPS123A1052 | https://www.mouser.co.uk/ProductDetail/OSRAM-Opto-Semiconductors/GR-JTLPS123-G7H4-45-1-150-R33?qs=T94vaHKWudSzDFhf8Pfs5w%3D%3D
 |  | D10 | GR_JTLPS1.23-G7H4-45-1-150-R33 | LED:GR_JTLPS1.23-G7H4-45-1-150-R33 | SamacSys_Parts:GRJTLPS123G7H4451150R33 | ~ | High Power LEDs - Single Color Red DURIS E 2835 | 0.8 | OSRAM | GR JTLPS1.23-G7H4-45-1-150-R33 | 720-GRJTLPS123A1052 | https://www.mouser.co.uk/ProductDetail/OSRAM-Opto-Semiconductors/GR-JTLPS123-G7H4-45-1-150-R33?qs=T94vaHKWudSzDFhf8Pfs5w%3D%3D
 |  | D11 | GR_JTLPS1.23-G7H4-45-1-150-R33 | LED:GR_JTLPS1.23-G7H4-45-1-150-R33 | SamacSys_Parts:GRJTLPS123G7H4451150R33 | ~ | High Power LEDs - Single Color Red DURIS E 2835 | 0.8 | OSRAM | GR JTLPS1.23-G7H4-45-1-150-R33 | 720-GRJTLPS123A1052 | https://www.mouser.co.uk/ProductDetail/OSRAM-Opto-Semiconductors/GR-JTLPS123-G7H4-45-1-150-R33?qs=T94vaHKWudSzDFhf8Pfs5w%3D%3D
 |  | D12 | GR_JTLPS1.23-G7H4-45-1-150-R33 | LED:GR_JTLPS1.23-G7H4-45-1-150-R33 | SamacSys_Parts:GRJTLPS123G7H4451150R33 | ~ | High Power LEDs - Single Color Red DURIS E 2835 | 0.8 | OSRAM | GR JTLPS1.23-G7H4-45-1-150-R33 | 720-GRJTLPS123A1052 | https://www.mouser.co.uk/ProductDetail/OSRAM-Opto-Semiconductors/GR-JTLPS123-G7H4-45-1-150-R33?qs=T94vaHKWudSzDFhf8Pfs5w%3D%3D
 |  | D13 | GR_JTLPS1.23-G7H4-45-1-150-R33 | LED:GR_JTLPS1.23-G7H4-45-1-150-R33 | SamacSys_Parts:GRJTLPS123G7H4451150R33 | ~ | High Power LEDs - Single Color Red DURIS E 2835 | 0.8 | OSRAM | GR JTLPS1.23-G7H4-45-1-150-R33 | 720-GRJTLPS123A1052 | https://www.mouser.co.uk/ProductDetail/OSRAM-Opto-Semiconductors/GR-JTLPS123-G7H4-45-1-150-R33?qs=T94vaHKWudSzDFhf8Pfs5w%3D%3D
 |  | D14 | GR_JTLPS1.23-G7H4-45-1-150-R33 | LED:GR_JTLPS1.23-G7H4-45-1-150-R33 | SamacSys_Parts:GRJTLPS123G7H4451150R33 | ~ | High Power LEDs - Single Color Red DURIS E 2835 | 0.8 | OSRAM | GR JTLPS1.23-G7H4-45-1-150-R33 | 720-GRJTLPS123A1052 | https://www.mouser.co.uk/ProductDetail/OSRAM-Opto-Semiconductors/GR-JTLPS123-G7H4-45-1-150-R33?qs=T94vaHKWudSzDFhf8Pfs5w%3D%3D
 |  | D15 | GR_JTLPS1.23-G7H4-45-1-150-R33 | LED:GR_JTLPS1.23-G7H4-45-1-150-R33 | SamacSys_Parts:GRJTLPS123G7H4451150R33 | ~ | High Power LEDs - Single Color Red DURIS E 2835 | 0.8 | OSRAM | GR JTLPS1.23-G7H4-45-1-150-R33 | 720-GRJTLPS123A1052 | https://www.mouser.co.uk/ProductDetail/OSRAM-Opto-Semiconductors/GR-JTLPS123-G7H4-45-1-150-R33?qs=T94vaHKWudSzDFhf8Pfs5w%3D%3D
 |  | D16 | GR_JTLPS1.23-G7H4-45-1-150-R33 | LED:GR_JTLPS1.23-G7H4-45-1-150-R33 | SamacSys_Parts:GRJTLPS123G7H4451150R33 | ~ | High Power LEDs - Single Color Red DURIS E 2835 | 0.8 | OSRAM | GR JTLPS1.23-G7H4-45-1-150-R33 | 720-GRJTLPS123A1052 | https://www.mouser.co.uk/ProductDetail/OSRAM-Opto-Semiconductors/GR-JTLPS123-G7H4-45-1-150-R33?qs=T94vaHKWudSzDFhf8Pfs5w%3D%3D
 |  | D17 | GR_JTLPS1.23-G7H4-45-1-150-R33 | LED:GR_JTLPS1.23-G7H4-45-1-150-R33 | SamacSys_Parts:GRJTLPS123G7H4451150R33 | ~ | High Power LEDs - Single Color Red DURIS E 2835 | 0.8 | OSRAM | GR JTLPS1.23-G7H4-45-1-150-R33 | 720-GRJTLPS123A1052 | https://www.mouser.co.uk/ProductDetail/OSRAM-Opto-Semiconductors/GR-JTLPS123-G7H4-45-1-150-R33?qs=T94vaHKWudSzDFhf8Pfs5w%3D%3D
 |  | D18 | GR_JTLPS1.23-G7H4-45-1-150-R33 | LED:GR_JTLPS1.23-G7H4-45-1-150-R33 | SamacSys_Parts:GRJTLPS123G7H4451150R33 | ~ | High Power LEDs - Single Color Red DURIS E 2835 | 0.8 | OSRAM | GR JTLPS1.23-G7H4-45-1-150-R33 | 720-GRJTLPS123A1052 | https://www.mouser.co.uk/ProductDetail/OSRAM-Opto-Semiconductors/GR-JTLPS123-G7H4-45-1-150-R33?qs=T94vaHKWudSzDFhf8Pfs5w%3D%3D
 |  | D19 | GR_JTLPS1.23-G7H4-45-1-150-R33 | LED:GR_JTLPS1.23-G7H4-45-1-150-R33 | SamacSys_Parts:GRJTLPS123G7H4451150R33 | ~ | High Power LEDs - Single Color Red DURIS E 2835 | 0.8 | OSRAM | GR JTLPS1.23-G7H4-45-1-150-R33 | 720-GRJTLPS123A1052 | https://www.mouser.co.uk/ProductDetail/OSRAM-Opto-Semiconductors/GR-JTLPS123-G7H4-45-1-150-R33?qs=T94vaHKWudSzDFhf8Pfs5w%3D%3D
 |  | D20 | GR_JTLPS1.23-G7H4-45-1-150-R33 | LED:GR_JTLPS1.23-G7H4-45-1-150-R33 | SamacSys_Parts:GRJTLPS123G7H4451150R33 | ~ | High Power LEDs - Single Color Red DURIS E 2835 | 0.8 | OSRAM | GR JTLPS1.23-G7H4-45-1-150-R33 | 720-GRJTLPS123A1052 | https://www.mouser.co.uk/ProductDetail/OSRAM-Opto-Semiconductors/GR-JTLPS123-G7H4-45-1-150-R33?qs=T94vaHKWudSzDFhf8Pfs5w%3D%3D
 |  | D21 | GR_JTLPS1.23-G7H4-45-1-150-R33 | LED:GR_JTLPS1.23-G7H4-45-1-150-R33 | SamacSys_Parts:GRJTLPS123G7H4451150R33 | ~ | High Power LEDs - Single Color Red DURIS E 2835 | 0.8 | OSRAM | GR JTLPS1.23-G7H4-45-1-150-R33 | 720-GRJTLPS123A1052 | https://www.mouser.co.uk/ProductDetail/OSRAM-Opto-Semiconductors/GR-JTLPS123-G7H4-45-1-150-R33?qs=T94vaHKWudSzDFhf8Pfs5w%3D%3D
 |  | D22 | GR_JTLPS1.23-G7H4-45-1-150-R33 | LED:GR_JTLPS1.23-G7H4-45-1-150-R33 | SamacSys_Parts:GRJTLPS123G7H4451150R33 | ~ | High Power LEDs - Single Color Red DURIS E 2835 | 0.8 | OSRAM | GR JTLPS1.23-G7H4-45-1-150-R33 | 720-GRJTLPS123A1052 | https://www.mouser.co.uk/ProductDetail/OSRAM-Opto-Semiconductors/GR-JTLPS123-G7H4-45-1-150-R33?qs=T94vaHKWudSzDFhf8Pfs5w%3D%3D
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

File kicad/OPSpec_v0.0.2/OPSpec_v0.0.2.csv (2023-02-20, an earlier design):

Source: | C:\School stuff\Bagby Lab\Projects\OPSpec\kicad\OPSpec_v0.0.2\OPSpec_v0.0.2.kicad_sch
Date: | 18/07/2022 15:21
Tool: | Eeschema (6.0.5)
Generator: | C:\Program Files\KiCad\6.0\bin\scripting\plugins/bom_csv_grouped_by_value.py
Component Count: | 153
Collated Components:
Item | Qty | Reference(s) | Value | LibPart | Footprint | Datasheet | Description | Height | Manufacturer_Name | Manufacturer_Part_Number | Mouser Part Number | Mouser Price/Stock
1 | 1 | A1 | Arduino_Nano_v3.x | MCU_Module:Arduino_Nano_v3.x | Module:Arduino_Nano | http://www.mouser.com/pdfdocs/Gravitech_Arduino_Nano3_0.pdf
2 | 4 | A2, A3, A4, A5 | TL074IDT | Amplifier_Operational:TL074IDT | SamacSys_Parts:SOIC127P600X175-14N | http://www.st.com/st-web-ui/static/active/en/resource/technical/document/datasheet/CD00000489.pdf | OP Amp Quad GP +/- 18V SOIC14 STMicroelectronics TL074IDT Quad Operational Amplifier, 3MHz, 14-Pin SO | 1.75 | STMicroelectronics | TL074IDT | 511-TL074IDT | https://www.mouser.co.uk/ProductDetail/STMicroelectronics/TL074IDT?qs=xiMLMHqF5JUaM%252BCWVyDQFA%3D%3D
3 | 2 | C1, C3 | 22uF | Device:C_Small | Capacitor_SMD:C_0805_2012Metric | ~
4 | 1 | C2 | 10uF | Device:C_Small | Capacitor_SMD:C_0805_2012Metric | ~
5 | 1 | C4 | 100nF | Device:C_Small | Capacitor_SMD:C_0805_2012Metric | ~
6 | 1 | C5 | 560p | Device:C_Small | Capacitor_SMD:C_0805_2012Metric | ~
7 | 2 | C6, C9 | 10uF | Device:C_Polarized_Small | Capacitor_Tantalum_SMD:CP_EIA-3216-10_Kemet-I | ~
8 | 1 | C7 | 100uF | Device:C_Polarized_Small | Capacitor_Tantalum_SMD:CP_EIA-6032-15_Kemet-U | ~
9 | 1 | C8 | 2n2F | Device:C_Small | Capacitor_SMD:C_0805_2012Metric | ~
10 | 16 | D1, D2, D3, D4, D5, D6, D7, D8, D9, D10, D11, D12, D13, D14, D15, D16 | GR_JTLPS1.23-G7H4-45-1-150-R33 | LED:GR_JTLPS1.23-G7H4-45-1-150-R33 | SamacSys_Parts:GRJTLPS123G7H4451150R33 | ~ | High Power LEDs - Single Color Red DURIS E 2835 | 0.8 | OSRAM | GR JTLPS1.23-G7H4-45-1-150-R33 | 720-GRJTLPS123A1052 | https://www.mouser.co.uk/ProductDetail/OSRAM-Opto-Semiconductors/GR-JTLPS123-G7H4-45-1-150-R33?qs=T94vaHKWudSzDFhf8Pfs5w%3D%3D
11 | 16 | D17, D18, D19, D20, D21, D22, D23, D24, D25, D26, D27, D28, D29, D30, D31, D32 | RB521S30T5G | Device:D_Schottky | SamacSys_Parts:SODFL1608X70N | ~ | Schottky Diodes & Rectifiers SCHOTTKY DIODE | 0.7 | onsemi | RB521S30T5G | 863-RB521S30T5G | https://www.mouser.co.uk/ProductDetail/onsemi/RB521S30T5G?qs=M3GgpExcU2%2FPpNUGuFHiAQ%3D%3D
12 | 8 | H1, H2, H3, H4, H5, H6, H7, H8 | MountingHole | Mechanical:MountingHole | MountingHole:MountingHole_2.5mm | ~
13 | 1 | IC1 | AP62301Z6-7 | SamacSys_Parts:AP62301Z6-7 | SamacSys_Parts:SOTFL50P162X60-6N | https://www.diodes.com/assets/Datasheets/AP62300_AP62301_AP62300T.pdf | DCDC CONV HV BUCK SOT563 T&R 3K 4.2V TO 18V INPUT, 3A LOW IQ SYNCHRONOUS BUCK CONVERTER | 0.6 | Diodes Inc. | AP62301Z6-7 | 621-AP62301Z6-7 | https://www.mouser.co.uk/ProductDetail/Diodes-Incorporated/AP62301Z6-7?qs=7MVldsJ5UawPLFx7TLBzhA%3D%3D
14 | 1 | IC2 | TA75S558F,LF | SamacSys_Parts:TA75S558F,LF | SamacSys_Parts:TA75S558FLF | https://toshiba.semicon-storage.com/info/docget.jsp?did=20986&prodName=TA75S558F | Operational Amplifiers - Op Amps Bipolar Op-Amp | 1.4 | Toshiba | TA75S558F,LF | 757-TA75S558FLF | https://www.mouser.co.uk/ProductDetail/Toshiba/TA75S558FLF?qs=lX6dEUlT%252BgcRNUil8WoaRA%3D%3D
15 | 1 | IC3 | ADR4550BRZ | SamacSys_Parts:ADR4550BRZ | SamacSys_Parts:SOIC127P600X175-8N | http://www.analog.com/media/en/technical-documentation/data-sheets/ADR4520_4525_4530_4533_4540_4550.pdf | Analog Devices ADR4550BRZ, Series Voltage Reference 5V, +/-0.02% 15 V max., 8-Pin SOIC | 1.75 | Analog Devices | ADR4550BRZ | 584-ADR4550BRZ | https://www.mouser.co.uk/ProductDetail/Analog-Devices/ADR4550BRZ?qs=WIvQP4zGangF4jmrnlRDgA%3D%3D
16 | 1 | IC4 | LT1054IPE4 | SamacSys_Parts:LT1054IPE4 | SamacSys_Parts:DIP794W53P254L959H508Q8N | https://www.ti.com/lit/ds/symlink/lt1054.pdf?ts=1606982687233 | Switching Voltage Regulators Switched-Capacitor Voltage Converter | 5.08 | Texas Instruments | LT1054IPE4 | 595-LT1054IPE4 | https://www.mouser.co.uk/ProductDetail/Texas-Instruments/LT1054IPE4?qs=paYhMW8qfivWYjyBPd45bA%3D%3D
17 | 1 | J1 | 163-179PH-EX | SamacSys_Parts:163-179PH-EX | SamacSys_Parts:163179PHEX | https://componentsearchengine.com/Datasheets/1/163-179PH-EX.pdf | DC Power Connectors PCB 2.1MM | 11 | Kobiconn | 163-179PH-EX | 163-179PH-EX | https://www.mouser.co.uk/ProductDetail/Kobiconn/163-179PH-EX?qs=Xb8IjHhkxj5l2UOaIqcGCw%3D%3D
18 | 1 | J2 | BASE_INTERFACE | Connector:Conn_01x07_Male | Connector_PinHeader_2.54mm:PinHeader_1x07_P2.54mm_Vertical | ~
19 | 1 | J3 | BASE_ADC_CH | Connector:Conn_01x08_Male | Connector_PinHeader_2.54mm:PinHeader_1x08_P2.54mm_Vertical | ~
20 | 1 | J4 | TOP_INTERFACE | Connector:Conn_01x07_Male | Connector_PinHeader_2.54mm:PinHeader_1x07_P2.54mm_Vertical | ~
21 | 1 | J5 | TOP_ADC_CH | Connector:Conn_01x08_Male | Connector_PinHeader_2.54mm:PinHeader_1x08_P2.54mm_Vertical | ~
22 | 1 | L1 | 3.3uH | SamacSys_Parts:MAKK2016T3R3M | SamacSys_Parts:INDPM2016X100N |  | Fixed Inductors 0806 3.3uH 255mOhms +/-20% 1150A HiCur | 1 | TAIYO YUDEN | MAKK2016T3R3M | 963-MAKK2016T3R3M | https://www.mouser.co.uk/ProductDetail/Taiyo-Yuden/MAKK2016T3R3M?qs=Z6svWd%2FY2UTQY1%2FASu%252BfUw%3D%3D
23 | 10 | Q1, Q2, Q3, Q4, Q5, Q6, Q7, Q8, Q11, Q12 | NXV75UP | Device:Q_PMOS_GSD | Package_TO_SOT_SMD:SOT-23 | ~
24 | 2 | Q9, Q10 | NTK3134NT5G | Device:Q_NMOS_GSD | SamacSys_Parts:NTK3134NT5G | https://www.onsemi.com/pdf/datasheet/ntk3134n-d.pdf | N-Channel 20 V 750mA (Ta) 310mW (Ta) Surface Mount SOT-723 | 0.55 | onsemi | NTK3134NT5G | 863-NTK3134NT5G | https://www.mouser.co.uk/ProductDetail/onsemi/NTK3134NT5G?qs=g97OBWmz8%2FWdltr4eSy1YA%3D%3D
25 | 16 | R1, R2, R3, R4, R5, R6, R7, R8, R9, R10, R11, R12, R13, R14, R15, R16 | 51R1 | Device:R_Small | Resistor_SMD:R_0603_1608Metric | ~
26 | 12 | R17, R18, R19, R20, R21, R22, R23, R24, R25, R26, R47, R48 | 150 | Device:R_Small | Resistor_SMD:R_0603_1608Metric | ~
27 | 2 | R27, R28 | 4.7k | Device:R_Small | Resistor_SMD:R_0603_1608Metric | ~
28 | 1 | R29 | 52.3k | Device:R_Small | Resistor_SMD:R_0603_1608Metric | ~
29 | 9 | R30, R51, R52, R53, R54, R55, R56, R57, R58 | 10k | Device:R_Small | Resistor_SMD:R_0603_1608Metric | ~
30 | 16 | R31, R32, R33, R34, R35, R36, R37, R38, R39, R40, R41, R42, R43, R44, R45, R46 | 2M55 | Device:R_Small | Resistor_SMD:R_0603_1608Metric | ~
31 | 1 | R49 | 88k7 | Device:R_Small | Resistor_SMD:R_0603_1608Metric | ~
32 | 1 | R50 | 1k1 | Device:R_Small | Resistor_SMD:R_0603_1608Metric | ~
33 | 1 | R59 | 102k | Device:R_Small | Resistor_SMD:R_0603_1608Metric | ~
34 | 1 | R60 | 20k | Device:R_Small | Resistor_SMD:R_0603_1608Metric | ~
35 | 16 | T1, T2, T3, T4, T5, T6, T7, T8, T9, T10, T11, T12, T13, T14, T15, T16 | SFH2716 A01 | Device:D_Photo | SamacSys_Parts:SFH2716 | ~
36 | 1 | U1 | ADS7828 | Analog_ADC:ADS7828 | Package_SO:TSSOP-16_4.4x5mm_P0.65mm | http://www.ti.com/lit/ds/symlink/ads7828.pdf
Individual Components:
Item | Qty | Reference(s) | Value | LibPart | Footprint | Datasheet | Description | Height | Manufacturer_Name | Manufacturer_Part_Number | Mouser Part Number | Mouser Price/Stock
 |  | A1 | Arduino_Nano_v3.x | MCU_Module:Arduino_Nano_v3.x | Module:Arduino_Nano | http://www.mouser.com/pdfdocs/Gravitech_Arduino_Nano3_0.pdf
 |  | A2 | TL074IDT | Amplifier_Operational:TL074IDT | SamacSys_Parts:SOIC127P600X175-14N | http://www.st.com/st-web-ui/static/active/en/resource/technical/document/datasheet/CD00000489.pdf | OP Amp Quad GP +/- 18V SOIC14 STMicroelectronics TL074IDT Quad Operational Amplifier, 3MHz, 14-Pin SO | 1.75 | STMicroelectronics | TL074IDT | 511-TL074IDT | https://www.mouser.co.uk/ProductDetail/STMicroelectronics/TL074IDT?qs=xiMLMHqF5JUaM%252BCWVyDQFA%3D%3D
 |  | A3 | TL074IDT | Amplifier_Operational:TL074IDT | SamacSys_Parts:SOIC127P600X175-14N | http://www.st.com/st-web-ui/static/active/en/resource/technical/document/datasheet/CD00000489.pdf | OP Amp Quad GP +/- 18V SOIC14 STMicroelectronics TL074IDT Quad Operational Amplifier, 3MHz, 14-Pin SO | 1.75 | STMicroelectronics | TL074IDT | 511-TL074IDT | https://www.mouser.co.uk/ProductDetail/STMicroelectronics/TL074IDT?qs=xiMLMHqF5JUaM%252BCWVyDQFA%3D%3D
 |  | A4 | TL074IDT | Amplifier_Operational:TL074IDT | SamacSys_Parts:SOIC127P600X175-14N | http://www.st.com/st-web-ui/static/active/en/resource/technical/document/datasheet/CD00000489.pdf | OP Amp Quad GP +/- 18V SOIC14 STMicroelectronics TL074IDT Quad Operational Amplifier, 3MHz, 14-Pin SO | 1.75 | STMicroelectronics | TL074IDT | 511-TL074IDT | https://www.mouser.co.uk/ProductDetail/STMicroelectronics/TL074IDT?qs=xiMLMHqF5JUaM%252BCWVyDQFA%3D%3D
 |  | A5 | TL074IDT | Amplifier_Operational:TL074IDT | SamacSys_Parts:SOIC127P600X175-14N | http://www.st.com/st-web-ui/static/active/en/resource/technical/document/datasheet/CD00000489.pdf | OP Amp Quad GP +/- 18V SOIC14 STMicroelectronics TL074IDT Quad Operational Amplifier, 3MHz, 14-Pin SO | 1.75 | STMicroelectronics | TL074IDT | 511-TL074IDT | https://www.mouser.co.uk/ProductDetail/STMicroelectronics/TL074IDT?qs=xiMLMHqF5JUaM%252BCWVyDQFA%3D%3D
 |  | C1 | 22uF | Device:C_Small | Capacitor_SMD:C_0805_2012Metric | ~
 |  | C2 | 10uF | Device:C_Small | Capacitor_SMD:C_0805_2012Metric | ~
 |  | C3 | 22uF | Device:C_Small | Capacitor_SMD:C_0805_2012Metric | ~
 |  | C4 | 100nF | Device:C_Small | Capacitor_SMD:C_0805_2012Metric | ~
 |  | C5 | 560p | Device:C_Small | Capacitor_SMD:C_0805_2012Metric | ~
 |  | C6 | 10uF | Device:C_Polarized_Small | Capacitor_Tantalum_SMD:CP_EIA-3216-10_Kemet-I | ~
 |  | C7 | 100uF | Device:C_Polarized_Small | Capacitor_Tantalum_SMD:CP_EIA-6032-15_Kemet-U | ~
 |  | C8 | 2n2 | Device:C_Small | Capacitor_SMD:C_0805_2012Metric | ~
 |  | C9 | 10uF | Device:C_Polarized_Small | Capacitor_Tantalum_SMD:CP_EIA-3216-10_Kemet-I | ~
 |  | D1 | GR_JTLPS1.23-G7H4-45-1-150-R33 | LED:GR_JTLPS1.23-G7H4-45-1-150-R33 | SamacSys_Parts:GRJTLPS123G7H4451150R33 | ~ | High Power LEDs - Single Color Red DURIS E 2835 | 0.8 | OSRAM | GR JTLPS1.23-G7H4-45-1-150-R33 | 720-GRJTLPS123A1052 | https://www.mouser.co.uk/ProductDetail/OSRAM-Opto-Semiconductors/GR-JTLPS123-G7H4-45-1-150-R33?qs=T94vaHKWudSzDFhf8Pfs5w%3D%3D
 |  | D2 | GR_JTLPS1.23-G7H4-45-1-150-R33 | LED:GR_JTLPS1.23-G7H4-45-1-150-R33 | SamacSys_Parts:GRJTLPS123G7H4451150R33 | ~ | High Power LEDs - Single Color Red DURIS E 2835 | 0.8 | OSRAM | GR JTLPS1.23-G7H4-45-1-150-R33 | 720-GRJTLPS123A1052 | https://www.mouser.co.uk/ProductDetail/OSRAM-Opto-Semiconductors/GR-JTLPS123-G7H4-45-1-150-R33?qs=T94vaHKWudSzDFhf8Pfs5w%3D%3D
 |  | D3 | GR_JTLPS1.23-G7H4-45-1-150-R33 | LED:GR_JTLPS1.23-G7H4-45-1-150-R33 | SamacSys_Parts:GRJTLPS123G7H4451150R33 | ~ | High Power LEDs - Single Color Red DURIS E 2835 | 0.8 | OSRAM | GR JTLPS1.23-G7H4-45-1-150-R33 | 720-GRJTLPS123A1052 | https://www.mouser.co.uk/ProductDetail/OSRAM-Opto-Semiconductors/GR-JTLPS123-G7H4-45-1-150-R33?qs=T94vaHKWudSzDFhf8Pfs5w%3D%3D
 |  | D4 | GR_JTLPS1.23-G7H4-45-1-150-R33 | LED:GR_JTLPS1.23-G7H4-45-1-150-R33 | SamacSys_Parts:GRJTLPS123G7H4451150R33 | ~ | High Power LEDs - Single Color Red DURIS E 2835 | 0.8 | OSRAM | GR JTLPS1.23-G7H4-45-1-150-R33 | 720-GRJTLPS123A1052 | https://www.mouser.co.uk/ProductDetail/OSRAM-Opto-Semiconductors/GR-JTLPS123-G7H4-45-1-150-R33?qs=T94vaHKWudSzDFhf8Pfs5w%3D%3D
 |  | D5 | GR_JTLPS1.23-G7H4-45-1-150-R33 | LED:GR_JTLPS1.23-G7H4-45-1-150-R33 | SamacSys_Parts:GRJTLPS123G7H4451150R33 | ~ | High Power LEDs - Single Color Red DURIS E 2835 | 0.8 | OSRAM | GR JTLPS1.23-G7H4-45-1-150-R33 | 720-GRJTLPS123A1052 | https://www.mouser.co.uk/ProductDetail/OSRAM-Opto-Semiconductors/GR-JTLPS123-G7H4-45-1-150-R33?qs=T94vaHKWudSzDFhf8Pfs5w%3D%3D
 |  | D6 | GR_JTLPS1.23-G7H4-45-1-150-R33 | LED:GR_JTLPS1.23-G7H4-45-1-150-R33 | SamacSys_Parts:GRJTLPS123G7H4451150R33 | ~ | High Power LEDs - Single Color Red DURIS E 2835 | 0.8 | OSRAM | GR JTLPS1.23-G7H4-45-1-150-R33 | 720-GRJTLPS123A1052 | https://www.mouser.co.uk/ProductDetail/OSRAM-Opto-Semiconductors/GR-JTLPS123-G7H4-45-1-150-R33?qs=T94vaHKWudSzDFhf8Pfs5w%3D%3D
 |  | D7 | GR_JTLPS1.23-G7H4-45-1-150-R33 | LED:GR_JTLPS1.23-G7H4-45-1-150-R33 | SamacSys_Parts:GRJTLPS123G7H4451150R33 | ~ | High Power LEDs - Single Color Red DURIS E 2835 | 0.8 | OSRAM | GR JTLPS1.23-G7H4-45-1-150-R33 | 720-GRJTLPS123A1052 | https://www.mouser.co.uk/ProductDetail/OSRAM-Opto-Semiconductors/GR-JTLPS123-G7H4-45-1-150-R33?qs=T94vaHKWudSzDFhf8Pfs5w%3D%3D
 |  | D8 | GR_JTLPS1.23-G7H4-45-1-150-R33 | LED:GR_JTLPS1.23-G7H4-45-1-150-R33 | SamacSys_Parts:GRJTLPS123G7H4451150R33 | ~ | High Power LEDs - Single Color Red DURIS E 2835 | 0.8 | OSRAM | GR JTLPS1.23-G7H4-45-1-150-R33 | 720-GRJTLPS123A1052 | https://www.mouser.co.uk/ProductDetail/OSRAM-Opto-Semiconductors/GR-JTLPS123-G7H4-45-1-150-R33?qs=T94vaHKWudSzDFhf8Pfs5w%3D%3D
 |  | D9 | GR_JTLPS1.23-G7H4-45-1-150-R33 | LED:GR_JTLPS1.23-G7H4-45-1-150-R33 | SamacSys_Parts:GRJTLPS123G7H4451150R33 | ~ | High Power LEDs - Single Color Red DURIS E 2835 | 0.8 | OSRAM | GR JTLPS1.23-G7H4-45-1-150-R33 | 720-GRJTLPS123A1052 | https://www.mouser.co.uk/ProductDetail/OSRAM-Opto-Semiconductors/GR-JTLPS123-G7H4-45-1-150-R33?qs=T94vaHKWudSzDFhf8Pfs5w%3D%3D
 |  | D10 | GR_JTLPS1.23-G7H4-45-1-150-R33 | LED:GR_JTLPS1.23-G7H4-45-1-150-R33 | SamacSys_Parts:GRJTLPS123G7H4451150R33 | ~ | High Power LEDs - Single Color Red DURIS E 2835 | 0.8 | OSRAM | GR JTLPS1.23-G7H4-45-1-150-R33 | 720-GRJTLPS123A1052 | https://www.mouser.co.uk/ProductDetail/OSRAM-Opto-Semiconductors/GR-JTLPS123-G7H4-45-1-150-R33?qs=T94vaHKWudSzDFhf8Pfs5w%3D%3D
 |  | D11 | GR_JTLPS1.23-G7H4-45-1-150-R33 | LED:GR_JTLPS1.23-G7H4-45-1-150-R33 | SamacSys_Parts:GRJTLPS123G7H4451150R33 | ~ | High Power LEDs - Single Color Red DURIS E 2835 | 0.8 | OSRAM | GR JTLPS1.23-G7H4-45-1-150-R33 | 720-GRJTLPS123A1052 | https://www.mouser.co.uk/ProductDetail/OSRAM-Opto-Semiconductors/GR-JTLPS123-G7H4-45-1-150-R33?qs=T94vaHKWudSzDFhf8Pfs5w%3D%3D
 |  | D12 | GR_JTLPS1.23-G7H4-45-1-150-R33 | LED:GR_JTLPS1.23-G7H4-45-1-150-R33 | SamacSys_Parts:GRJTLPS123G7H4451150R33 | ~ | High Power LEDs - Single Color Red DURIS E 2835 | 0.8 | OSRAM | GR JTLPS1.23-G7H4-45-1-150-R33 | 720-GRJTLPS123A1052 | https://www.mouser.co.uk/ProductDetail/OSRAM-Opto-Semiconductors/GR-JTLPS123-G7H4-45-1-150-R33?qs=T94vaHKWudSzDFhf8Pfs5w%3D%3D
 |  | D13 | GR_JTLPS1.23-G7H4-45-1-150-R33 | LED:GR_JTLPS1.23-G7H4-45-1-150-R33 | SamacSys_Parts:GRJTLPS123G7H4451150R33 | ~ | High Power LEDs - Single Color Red DURIS E 2835 | 0.8 | OSRAM | GR JTLPS1.23-G7H4-45-1-150-R33 | 720-GRJTLPS123A1052 | https://www.mouser.co.uk/ProductDetail/OSRAM-Opto-Semiconductors/GR-JTLPS123-G7H4-45-1-150-R33?qs=T94vaHKWudSzDFhf8Pfs5w%3D%3D
 |  | D14 | GR_JTLPS1.23-G7H4-45-1-150-R33 | LED:GR_JTLPS1.23-G7H4-45-1-150-R33 | SamacSys_Parts:GRJTLPS123G7H4451150R33 | ~ | High Power LEDs - Single Color Red DURIS E 2835 | 0.8 | OSRAM | GR JTLPS1.23-G7H4-45-1-150-R33 | 720-GRJTLPS123A1052 | https://www.mouser.co.uk/ProductDetail/OSRAM-Opto-Semiconductors/GR-JTLPS123-G7H4-45-1-150-R33?qs=T94vaHKWudSzDFhf8Pfs5w%3D%3D
 |  | D15 | GR_JTLPS1.23-G7H4-45-1-150-R33 | LED:GR_JTLPS1.23-G7H4-45-1-150-R33 | SamacSys_Parts:GRJTLPS123G7H4451150R33 | ~ | High Power LEDs - Single Color Red DURIS E 2835 | 0.8 | OSRAM | GR JTLPS1.23-G7H4-45-1-150-R33 | 720-GRJTLPS123A1052 | https://www.mouser.co.uk/ProductDetail/OSRAM-Opto-Semiconductors/GR-JTLPS123-G7H4-45-1-150-R33?qs=T94vaHKWudSzDFhf8Pfs5w%3D%3D
 |  | D16 | GR_JTLPS1.23-G7H4-45-1-150-R33 | LED:GR_JTLPS1.23-G7H4-45-1-150-R33 | SamacSys_Parts:GRJTLPS123G7H4451150R33 | ~ | High Power LEDs - Single Color Red DURIS E 2835 | 0.8 | OSRAM | GR JTLPS1.23-G7H4-45-1-150-R33 | 720-GRJTLPS123A1052 | https://www.mouser.co.uk/ProductDetail/OSRAM-Opto-Semiconductors/GR-JTLPS123-G7H4-45-1-150-R33?qs=T94vaHKWudSzDFhf8Pfs5w%3D%3D
 |  | D17 | RB521S30T5G | Device:D_Schottky | SamacSys_Parts:SODFL1608X70N | ~ | Schottky Diodes & Rectifiers SCHOTTKY DIODE | 0.7 | onsemi | RB521S30T5G | 863-RB521S30T5G | https://www.mouser.co.uk/ProductDetail/onsemi/RB521S30T5G?qs=M3GgpExcU2%2FPpNUGuFHiAQ%3D%3D
 |  | D18 | RB521S30T5G | Device:D_Schottky | SamacSys_Parts:SODFL1608X70N | ~ | Schottky Diodes & Rectifiers SCHOTTKY DIODE | 0.7 | onsemi | RB521S30T5G | 863-RB521S30T5G | https://www.mouser.co.uk/ProductDetail/onsemi/RB521S30T5G?qs=M3GgpExcU2%2FPpNUGuFHiAQ%3D%3D
 |  | D19 | RB521S30T5G | Device:D_Schottky | SamacSys_Parts:SODFL1608X70N | ~ | Schottky Diodes & Rectifiers SCHOTTKY DIODE | 0.7 | onsemi | RB521S30T5G | 863-RB521S30T5G | https://www.mouser.co.uk/ProductDetail/onsemi/RB521S30T5G?qs=M3GgpExcU2%2FPpNUGuFHiAQ%3D%3D
 |  | D20 | RB521S30T5G | Device:D_Schottky | SamacSys_Parts:SODFL1608X70N | ~ | Schottky Diodes & Rectifiers SCHOTTKY DIODE | 0.7 | onsemi | RB521S30T5G | 863-RB521S30T5G | https://www.mouser.co.uk/ProductDetail/onsemi/RB521S30T5G?qs=M3GgpExcU2%2FPpNUGuFHiAQ%3D%3D
 |  | D21 | RB521S30T5G | Device:D_Schottky | SamacSys_Parts:SODFL1608X70N | ~ | Schottky Diodes & Rectifiers SCHOTTKY DIODE | 0.7 | onsemi | RB521S30T5G | 863-RB521S30T5G | https://www.mouser.co.uk/ProductDetail/onsemi/RB521S30T5G?qs=M3GgpExcU2%2FPpNUGuFHiAQ%3D%3D
 |  | D22 | RB521S30T5G | Device:D_Schottky | SamacSys_Parts:SODFL1608X70N | ~ | Schottky Diodes & Rectifiers SCHOTTKY DIODE | 0.7 | onsemi | RB521S30T5G | 863-RB521S30T5G | https://www.mouser.co.uk/ProductDetail/onsemi/RB521S30T5G?qs=M3GgpExcU2%2FPpNUGuFHiAQ%3D%3D
 |  | D23 | RB521S30T5G | Device:D_Schottky | SamacSys_Parts:SODFL1608X70N | ~ | Schottky Diodes & Rectifiers SCHOTTKY DIODE | 0.7 | onsemi | RB521S30T5G | 863-RB521S30T5G | https://www.mouser.co.uk/ProductDetail/onsemi/RB521S30T5G?qs=M3GgpExcU2%2FPpNUGuFHiAQ%3D%3D
 |  | D24 | RB521S30T5G | Device:D_Schottky | SamacSys_Parts:SODFL1608X70N | ~ | Schottky Diodes & Rectifiers SCHOTTKY DIODE | 0.7 | onsemi | RB521S30T5G | 863-RB521S30T5G | https://www.mouser.co.uk/ProductDetail/onsemi/RB521S30T5G?qs=M3GgpExcU2%2FPpNUGuFHiAQ%3D%3D
 |  | D25 | RB521S30T5G | Device:D_Schottky | SamacSys_Parts:SODFL1608X70N | ~ | Schottky Diodes & Rectifiers SCHOTTKY DIODE | 0.7 | onsemi | RB521S30T5G | 863-RB521S30T5G | https://www.mouser.co.uk/ProductDetail/onsemi/RB521S30T5G?qs=M3GgpExcU2%2FPpNUGuFHiAQ%3D%3D
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

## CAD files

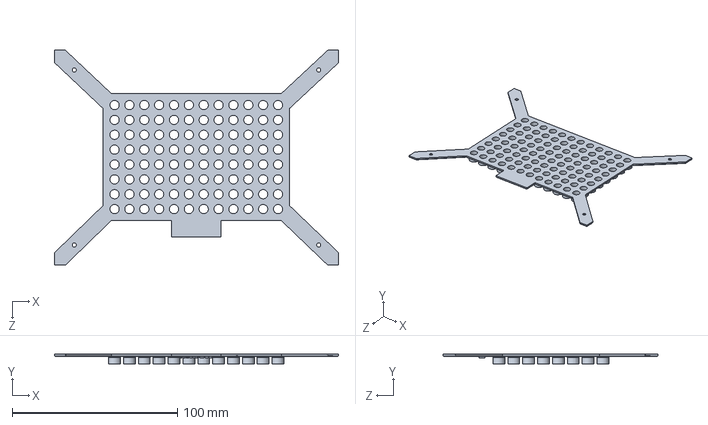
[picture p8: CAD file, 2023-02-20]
housing/test_board/LED_grid.SLDPRT
172.0 x 6.00 x 130.0 mm

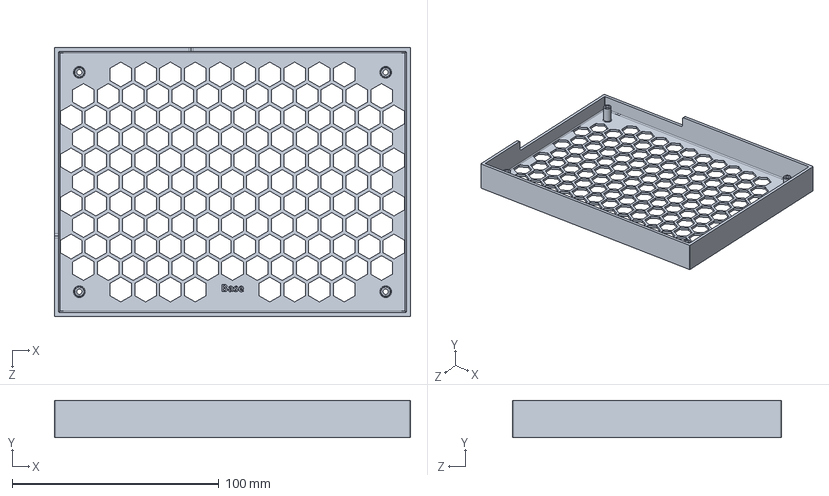
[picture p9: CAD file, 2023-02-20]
housing/test_board/base_plate.SLDPRT
172.0 x 18.1 x 130.0 mm

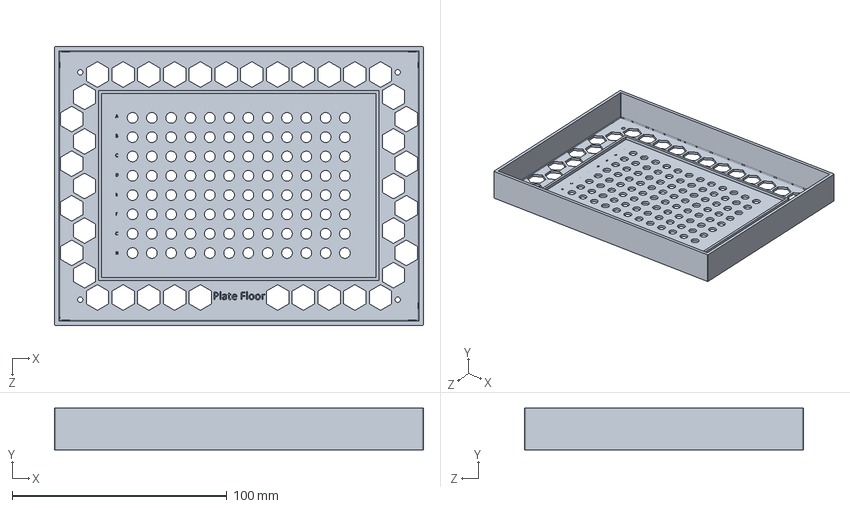
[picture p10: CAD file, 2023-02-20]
housing/test_board/plate_floor.SLDPRT
172.0 x 19.5 x 130.0 mm

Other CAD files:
housing/test_board/STLs/base_plate.STL
housing/test_board/STLs/plate_floor.STL

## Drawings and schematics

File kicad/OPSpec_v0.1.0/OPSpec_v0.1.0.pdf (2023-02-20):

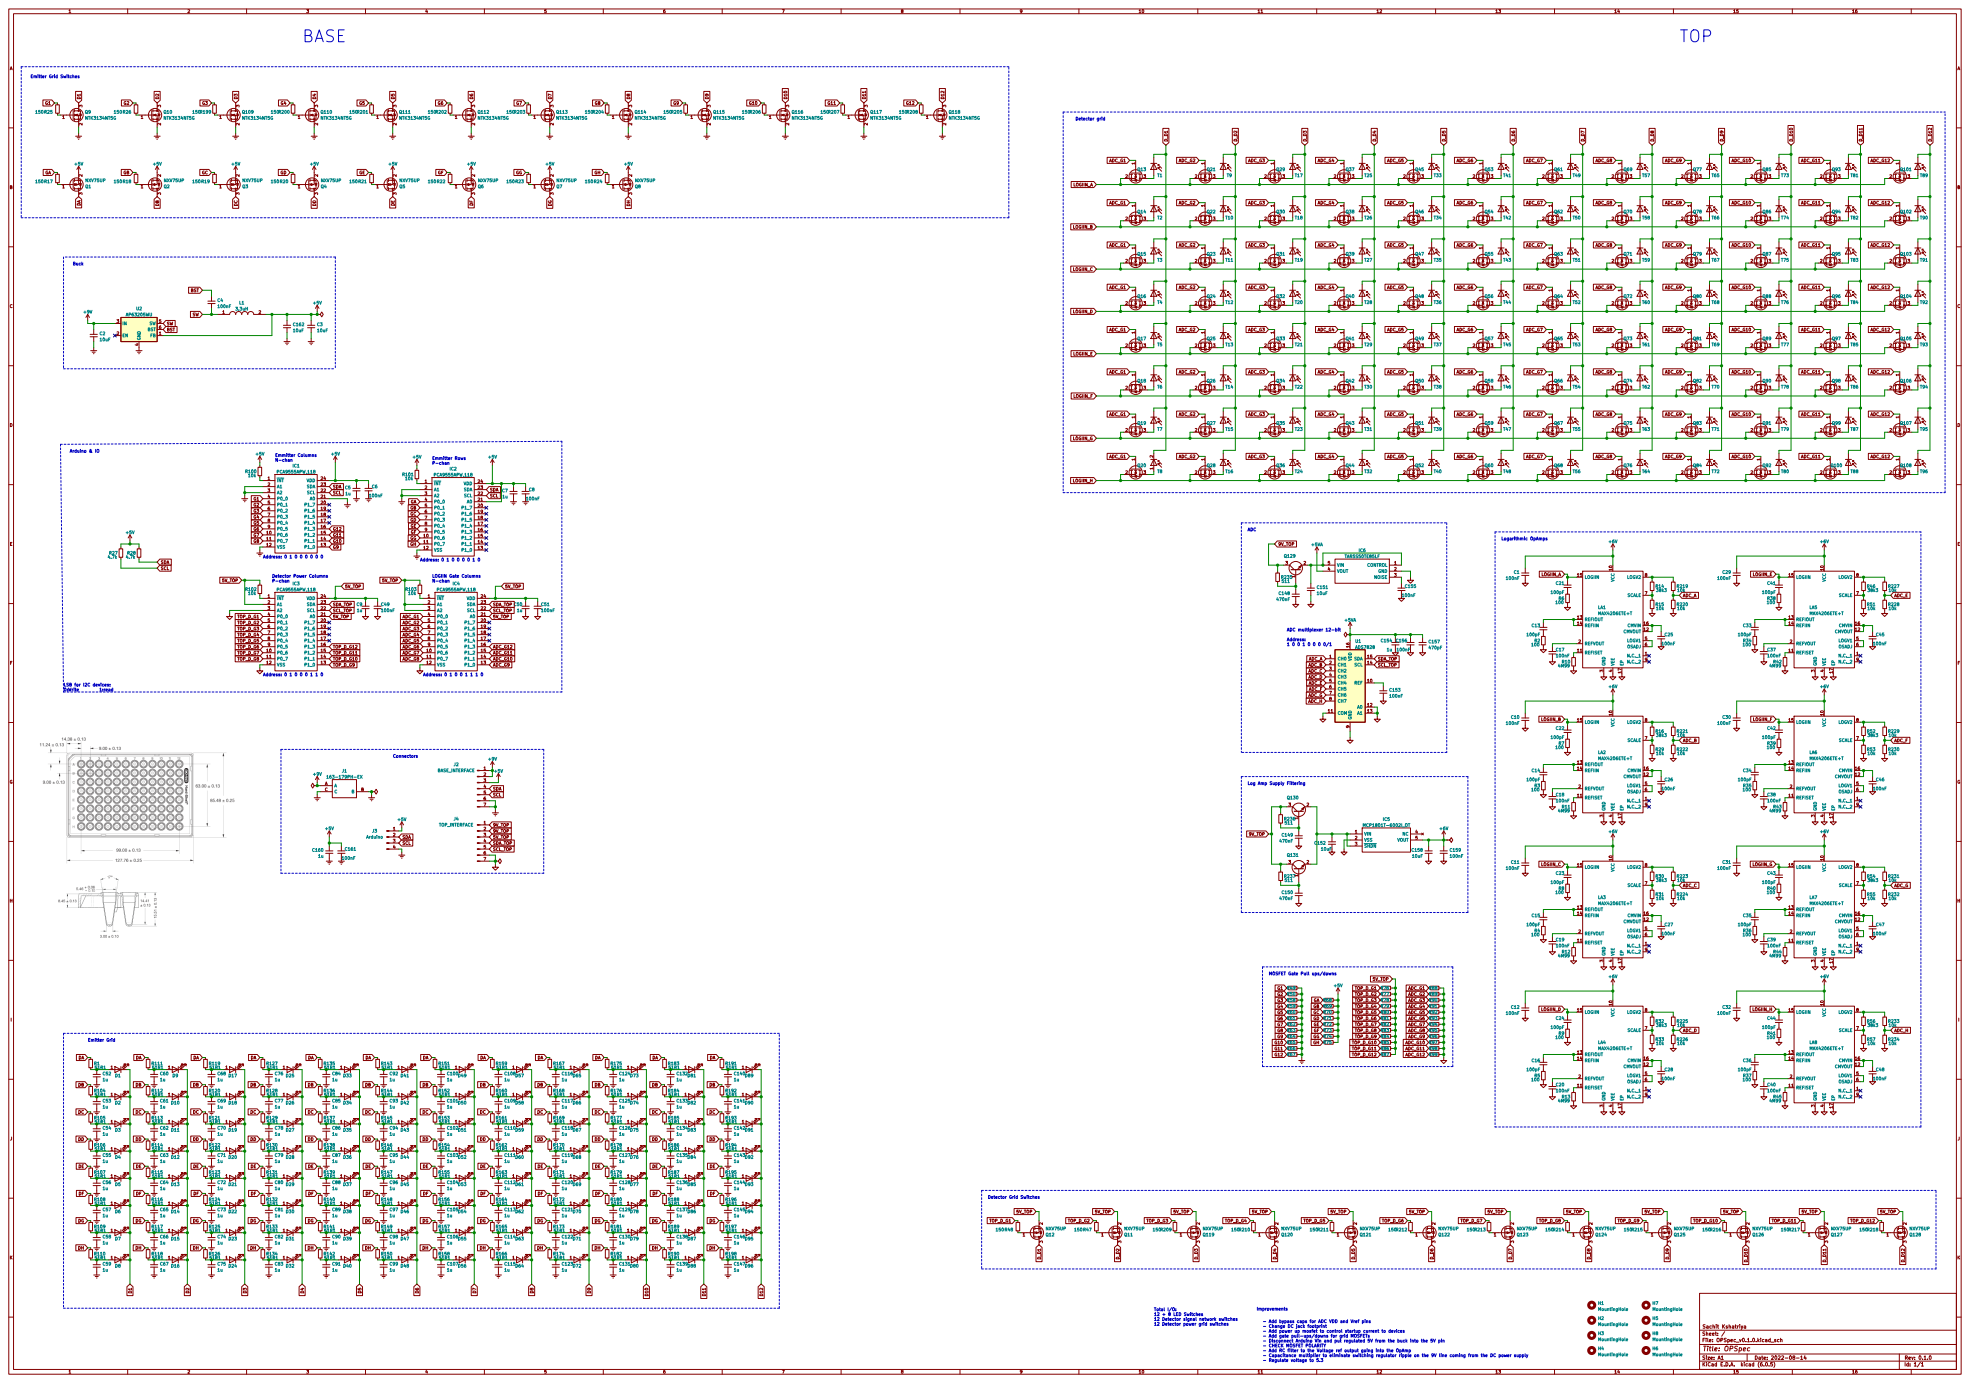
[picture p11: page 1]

Emmitter Columns N-chan Address: 0 1 0 0 0 0 0 0
Emmitter Rows P-chan Connectors

SCL SDA GAGE GDGBGCGF GG

LOGIIN Gate Columns N-chan Address: 0 1 0 0 0 1 1 0

Detector Power Columns P-chan

LSB for I2C devices: 0:Write 1:read

Log Amp Supply Filtering

Total I/O: 12 + 8 LED Switches 12 Detector signal network switches

12 Detector power grid switches

- Add bypass caps for ADC VDD and Vref pins
- Change DC jack footprint
- Add power up mosfet to control startup current to devices
- Add gate pull-ups/downs for grid MOSFETs
- Disconnect Arduino Vin and put regulated 5V from the buck into the 5V pin
- CHECK MOSFET POLARITY
- Add RC filter to the Voltage ref output going into the OpAmp
- Capacitance multiplier to eliminate switching regulator ripple on the 9V line coming from the DC power supply

File: OPSpec_v0.1.0.kicad_sch Sheet: / Sachit Kshatriya

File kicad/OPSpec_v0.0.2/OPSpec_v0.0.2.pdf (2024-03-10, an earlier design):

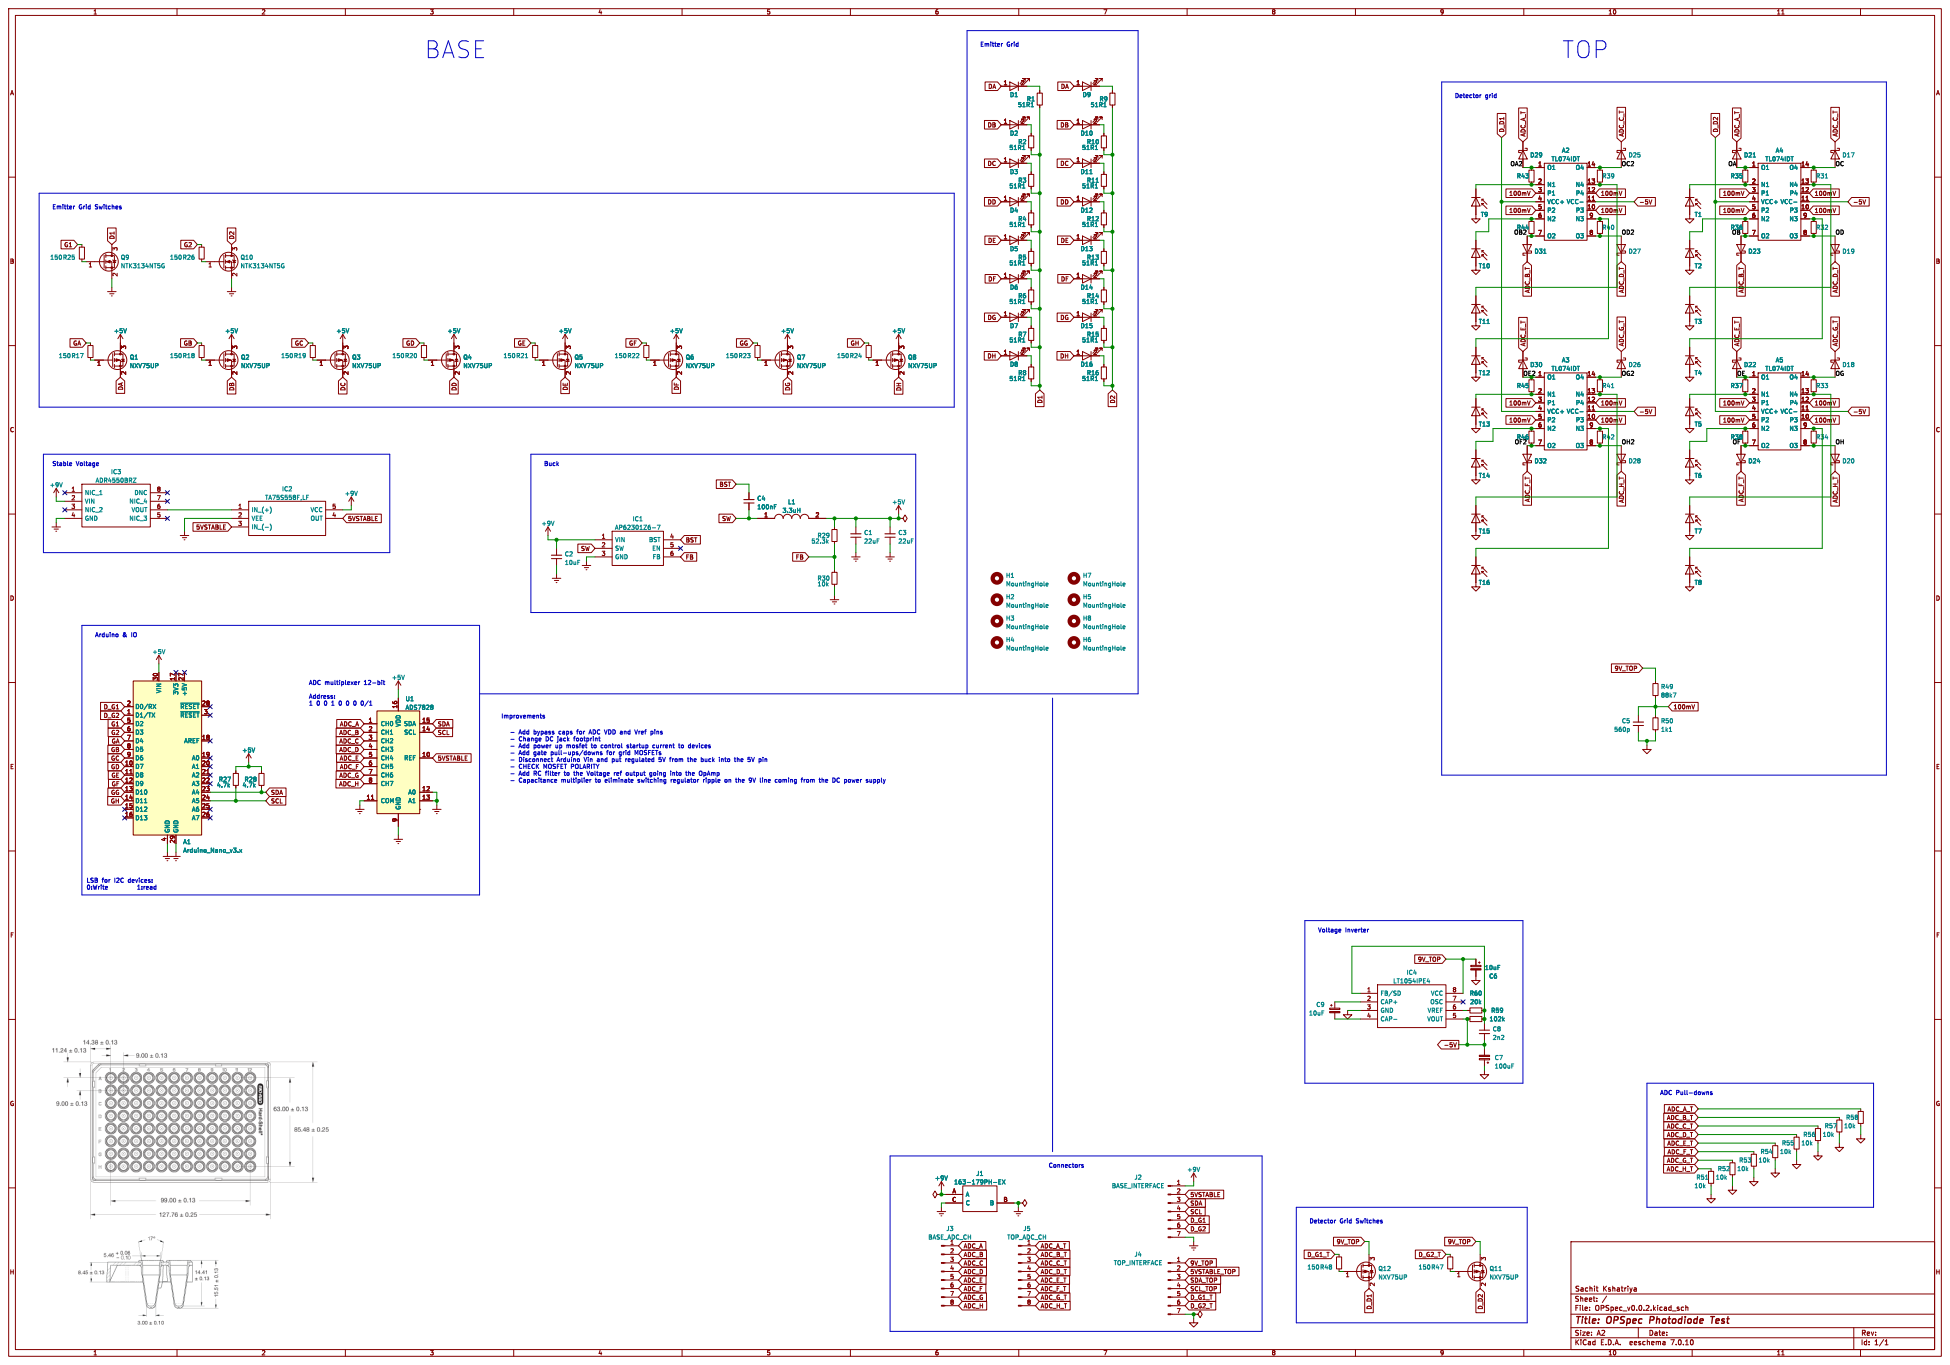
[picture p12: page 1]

- Add bypass caps for ADC VDD and Vref pins

- CHECK MOSFET POLARITY
- Add RC filter to the Voltage ref output going into the OpAmp

LSB for I2C devices: 0:Write 1:read

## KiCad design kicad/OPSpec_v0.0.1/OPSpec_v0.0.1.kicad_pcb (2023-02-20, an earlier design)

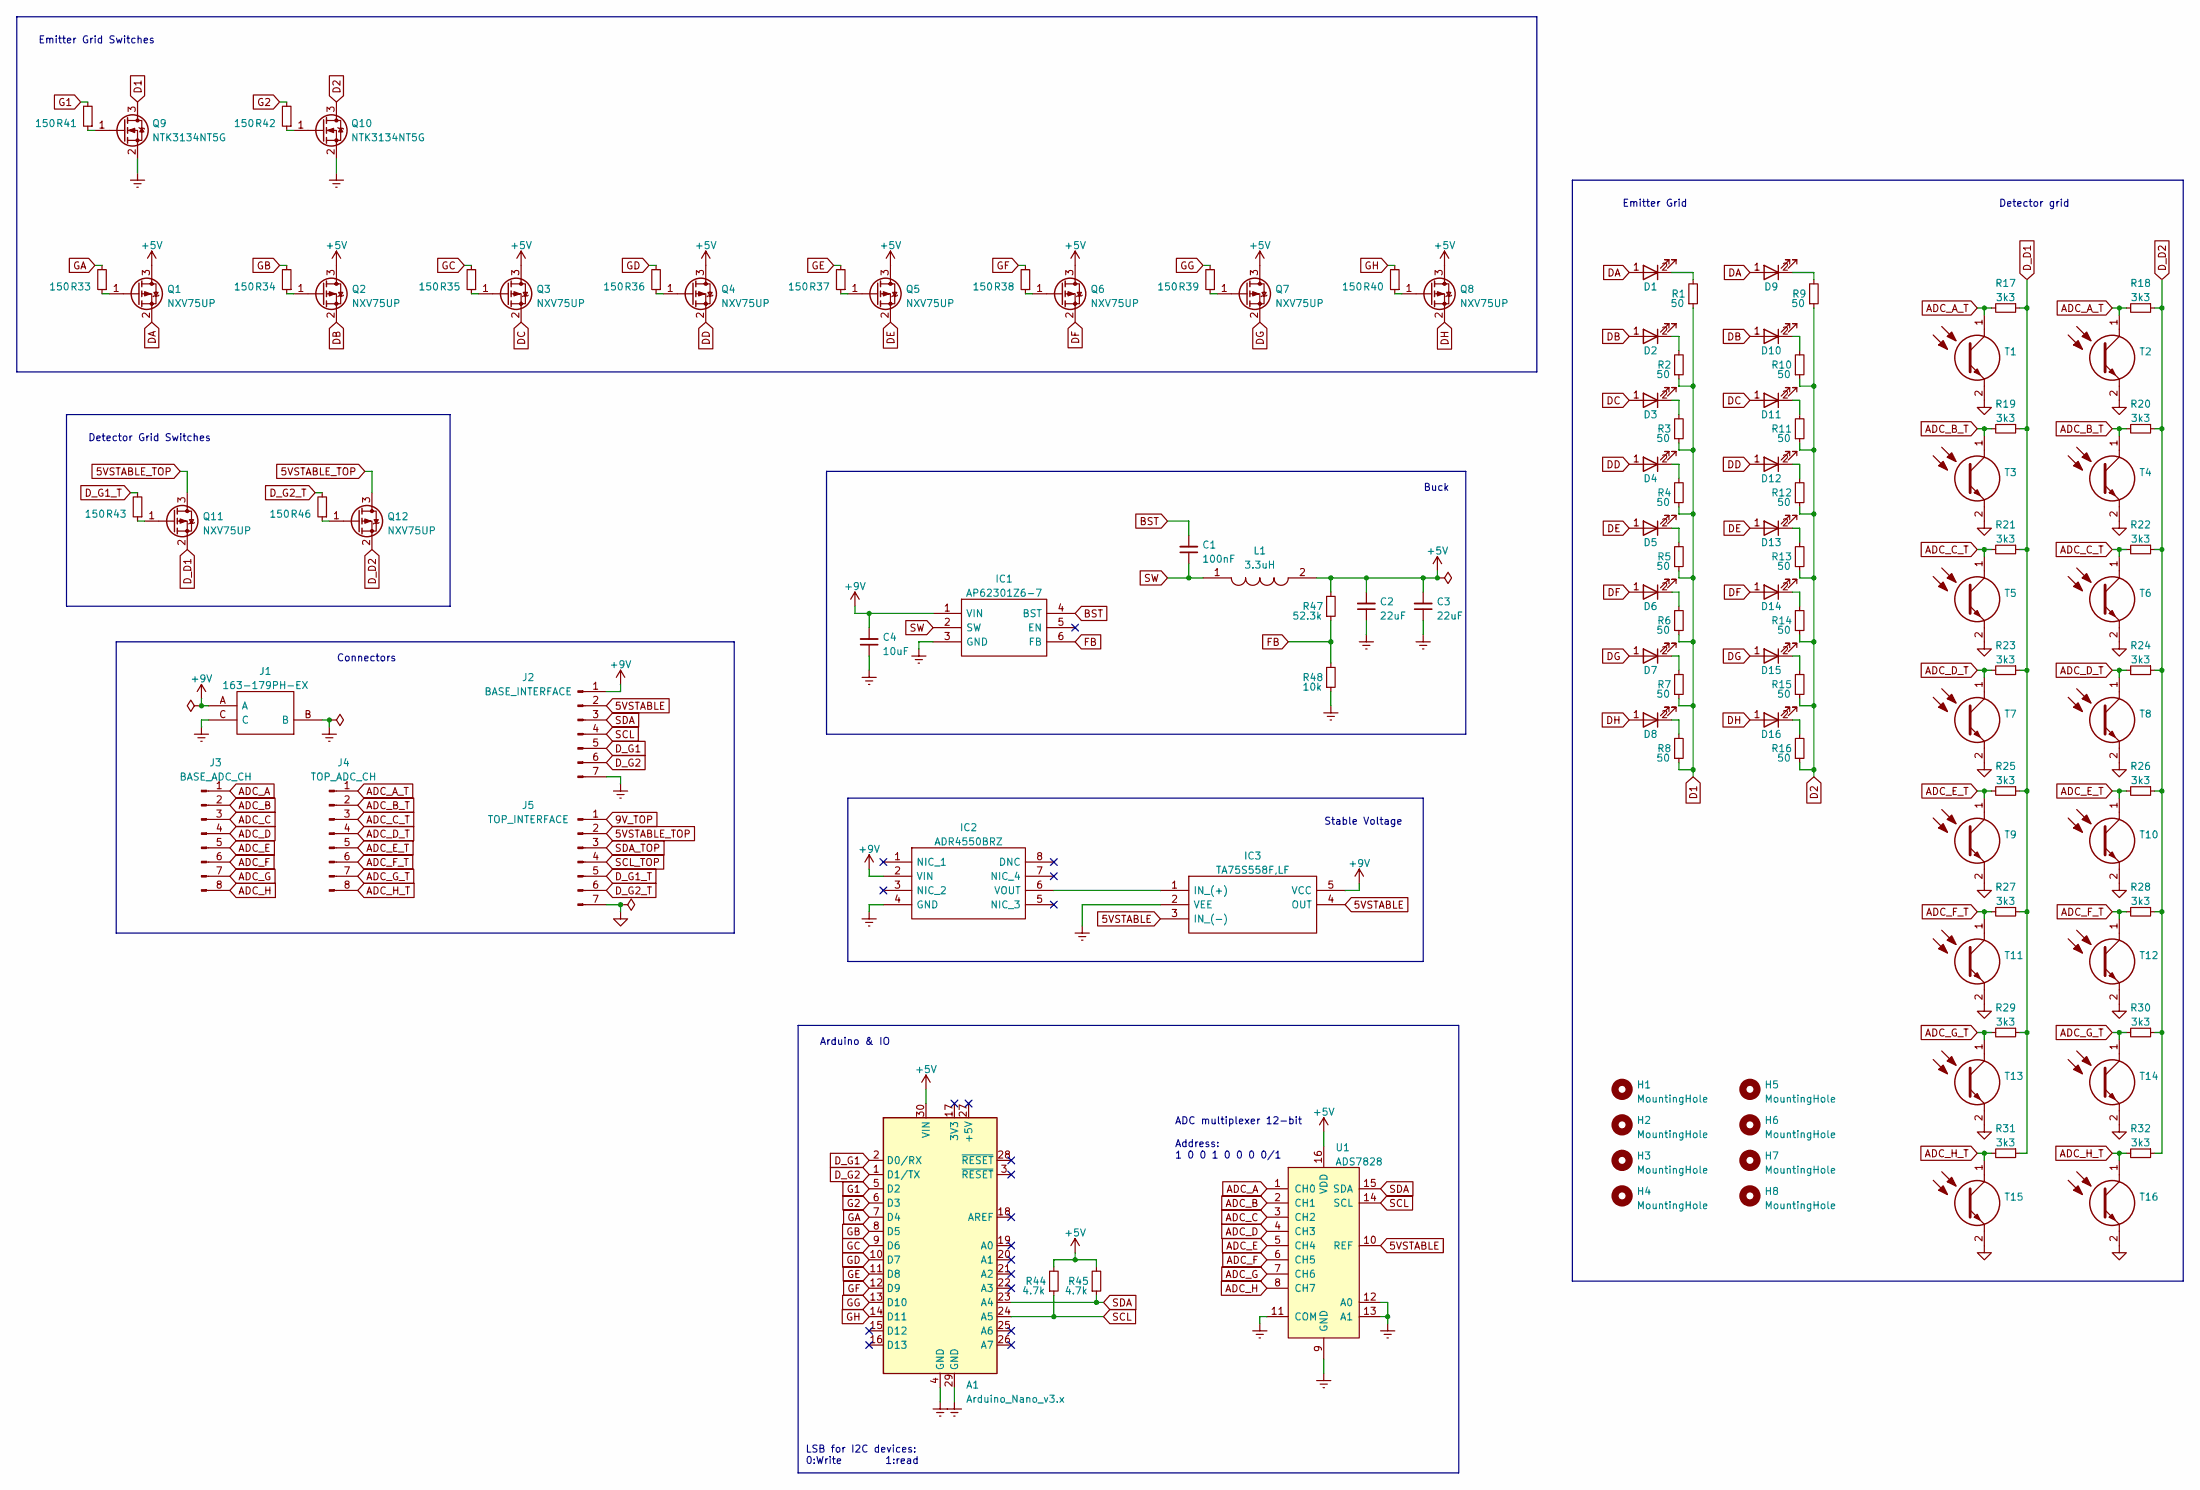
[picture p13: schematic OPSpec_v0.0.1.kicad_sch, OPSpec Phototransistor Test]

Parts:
A1: Arduino_Nano_v3.x; Arduino_Nano
C1: 100nF; C_0805_2012Metric
C2, C3: 22uF; C_0805_2012Metric
C4: 10uF; C_0805_2012Metric
D1, D2, D3, D4, D5, D6, D7, D8, D9, D10, D11, D12, D13, D14, D15, D16: GR_JTLPS1.23-G7H4-45-1-150-R33; GRJTLPS123G7H4451150R33; Mouser Part Number 720-GRJTLPS123A1052
H1, H2, H3, H4, H5, H6, H7, H8: MountingHole; MountingHole_2.5mm
IC1: AP62301Z6-7; SOTFL50P162X60-6N; Mouser Part Number 621-AP62301Z6-7
IC2: ADR4550BRZ; SOIC127P600X175-8N; Mouser Part Number 584-ADR4550BRZ
IC3: TA75S558F,LF; TA75S558FLF; Mouser Part Number 757-TA75S558FLF
J1: 163-179PH-EX; 163179PHEX; Mouser Part Number 163-179PH-EX
J2: BASE_INTERFACE; PinHeader_1x07_P2.54mm_Vertical
J3: BASE_ADC_CH; PinHeader_1x08_P2.54mm_Vertical
J4: TOP_ADC_CH; PinHeader_1x08_P2.54mm_Vertical
J5: TOP_INTERFACE; PinHeader_1x07_P2.54mm_Vertical
L1: 3.3uH; INDPM2016X100N; Mouser Part Number 963-MAKK2016T3R3M
Q1, Q2, Q3, Q4, Q5, Q6, Q7, Q8, Q11, Q12: NXV75UP; SOT-23
Q9, Q10: NTK3134NT5G; Mouser Part Number 863-NTK3134NT5G
R1, R2, R3, R4, R5, R6, R7, R8, R9, R10, R11, R12, R13, R14, R15, R16: 50; R_0603_1608Metric
R17, R18, R19, R20, R21, R22, R23, R24, R25, R26, R27, R28, R29, R30, R31, R32: 3k3; R_0603_1608Metric
R33, R34, R35, R36, R37, R38, R39, R40, R41, R42, R43, R46: 150; R_0603_1608Metric
R44, R45: 4.7k; R_0603_1608Metric
R47: 52.3k; R_0603_1608Metric
R48: 10k; R_0603_1608Metric
T1, T2, T3, T4, T5, T6, T7, T8, T9, T10, T11, T12, T13, T14, T15, T16: KDT00030TR; Mouser Part Number 512-KDT00030TR
U1: ADS7828; TSSOP-16_4.4x5mm_P0.65mm

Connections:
5VSTABLE: IC3.3 (IN_(-)), IC3.4 (OUT), J2.2, U1.10 (REF)
5VSTABLE_TOP: J5.2, Q11.3 (D), Q12.3 (D)
9V_TOP: J5.1
+5V: A1.30 (VIN), C2.2, C3.2, L1.2, Q1.3 (D), Q2.3 (D), Q3.3 (D), Q4.3 (D), Q5.3 (D), Q6.3 (D), Q7.3 (D), Q8.3 (D), R44.2, R45.2, R47.2, U1.16 (VDD)
+9V: C4.2, IC1.1 (VIN), IC2.2 (VIN), IC3.5 (VCC), J1.A, J2.1
ADC_A: J3.1, U1.1 (CH0)
ADC_A_T: J4.1, R17.2, R18.2, T1.1 (C), T2.1 (C)
ADC_B: J3.2, U1.2 (CH1)
ADC_B_T: J4.2, R19.2, R20.2, T3.1 (C), T4.1 (C)
ADC_C: J3.3, U1.3 (CH2)
ADC_C_T: J4.3, R21.2, R22.2, T5.1 (C), T6.1 (C)
ADC_D: J3.4, U1.4 (CH3)
ADC_D_T: J4.4, R23.2, R24.2, T7.1 (C), T8.1 (C)
ADC_E: J3.5, U1.5 (CH4)
ADC_E_T: J4.5, R25.2, R26.2, T9.1 (C), T10.1 (C)
ADC_F: J3.6, U1.6 (CH5)
ADC_F_T: J4.6, R27.2, R28.2, T11.1 (C), T12.1 (C)
ADC_G: J3.7, U1.7 (CH6)
ADC_G_T: J4.7, R29.2, R30.2, T13.1 (C), T14.1 (C)
ADC_H: J3.8, U1.8 (CH7)
ADC_H_T: J4.8, R31.2, R32.2, T15.1 (C), T16.1 (C)
BST: C1.2, IC1.4 (BST)
D1: Q9.3 (D), R1.1, R2.1, R3.1, R4.1, R5.1, R6.1, R7.1, R8.1
D2: Q10.3 (D), R9.1, R10.1, R11.1, R12.1, R13.1, R14.1, R15.1, R16.1
DA: D1.1 (A), D9.1 (A), Q1.2 (S)
DB: D2.1 (A), D10.1 (A), Q2.2 (S)
DC: D3.1 (A), D11.1 (A), Q3.2 (S)
DD: D4.1 (A), D12.1 (A), Q4.2 (S)
DE: D5.1 (A), D13.1 (A), Q5.2 (S)
DF: D6.1 (A), D14.1 (A), Q6.2 (S)
DG: D7.1 (A), D15.1 (A), Q7.2 (S)
DH: D8.1 (A), D16.1 (A), Q8.2 (S)
D_D1: Q11.2 (S), R17.1, R19.1, R21.1, R23.1, R25.1, R27.1, R29.1, R31.1
D_D2: Q12.2 (S), R18.1, R20.1, R22.1, R24.1, R26.1, R28.1, R30.1, R32.1
D_G1: A1.2 (D0/RX), J2.5
D_G1_T: J5.5, R43.2
D_G2: A1.1 (D1/TX), J2.6
D_G2_T: J5.6, R46.2
Earth: A1.4 (GND), A1.29 (GND), C2.1, C3.1, C4.1, IC1.3 (GND), IC2.4 (GND), IC3.2 (VEE), J1.B, J1.C, J2.7, Q9.2 (S), Q10.2 (S), R48.1, U1.9 (GND), U1.11 (COM), U1.12 (A0), U1.13 (A1)
FB: IC1.6 (FB), R47.1, R48.2
G1: A1.5 (D2), R41.2
G2: A1.6 (D3), R42.2
GA: A1.7 (D4), R33.2
GB: A1.8 (D5), R34.2
GC: A1.9 (D6), R35.2
GD: A1.10 (D7), R36.2
GE: A1.11 (D8), R37.2
GF: A1.12 (D9), R38.2
GG: A1.13 (D10), R39.2
GH: A1.14 (D11), R40.2
GND: J5.7, T1.2 (E), T2.2 (E), T3.2 (E), T4.2 (E), T5.2 (E), T6.2 (E), T7.2 (E), T8.2 (E), T9.2 (E), T10.2 (E), T11.2 (E), T12.2 (E), T13.2 (E), T14.2 (E), T15.2 (E), T16.2 (E)
unnamed: D1.2 (K), R1.2
unnamed: D2.2 (K), R2.2
unnamed: D3.2 (K), R3.2
unnamed: D4.2 (K), R4.2
unnamed: D5.2 (K), R5.2
unnamed: D6.2 (K), R6.2
unnamed: D7.2 (K), R7.2
unnamed: D8.2 (K), R8.2
unnamed: D9.2 (K), R9.2
unnamed: D10.2 (K), R10.2
unnamed: D11.2 (K), R11.2
unnamed: D12.2 (K), R12.2
unnamed: D13.2 (K), R13.2
unnamed: D14.2 (K), R14.2
unnamed: D15.2 (K), R15.2
unnamed: D16.2 (K), R16.2
unnamed: IC2.6 (VOUT), IC3.1 (IN_(+))
unnamed: Q1.1 (G), R33.1
unnamed: Q2.1 (G), R34.1
unnamed: Q3.1 (G), R35.1
unnamed: Q4.1 (G), R36.1
unnamed: Q5.1 (G), R37.1
unnamed: Q6.1 (G), R38.1
unnamed: Q7.1 (G), R39.1
unnamed: Q8.1 (G), R40.1
unnamed: Q9.1 (G), R41.1
unnamed: Q10.1 (G), R42.1
unnamed: Q11.1 (G), R43.1
unnamed: Q12.1 (G), R46.1
SCL: A1.24 (A5), J2.4, R44.1, U1.14 (SCL)
SCL_TOP: J5.4
SDA: A1.23 (A4), J2.3, R45.1, U1.15 (SDA)
SDA_TOP: J5.3
SW: C1.1, IC1.2 (SW), L1.1

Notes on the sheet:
ADC multiplexer 12-bit Address: 1 0 0 1 0 0 0 0/1
Arduino & IO
Connectors
Detector Grid Switches
Emitter Grid Switches
Detector grid
Buck
LSB for I2C devices: 0:Write 1:read
Emitter Grid
Stable Voltage

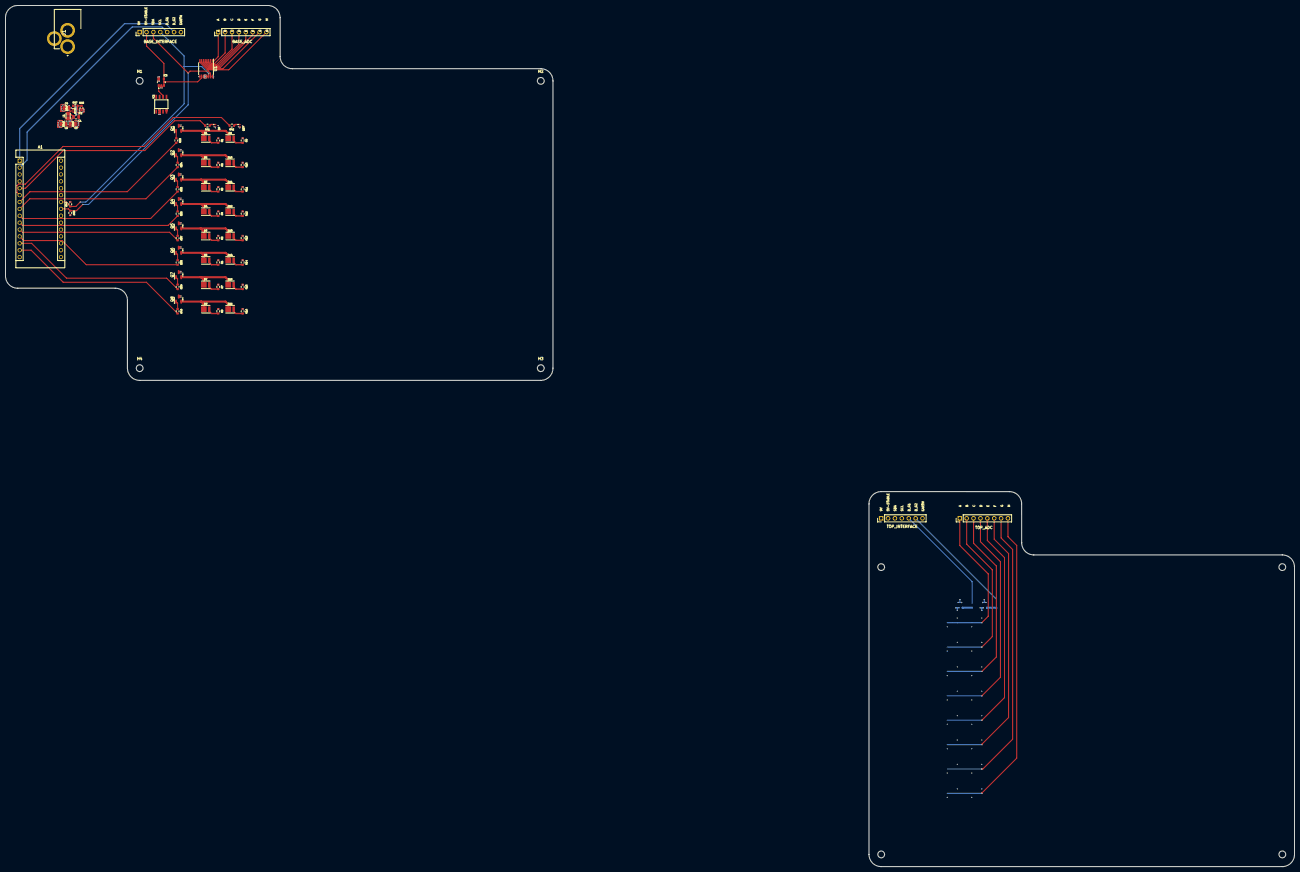
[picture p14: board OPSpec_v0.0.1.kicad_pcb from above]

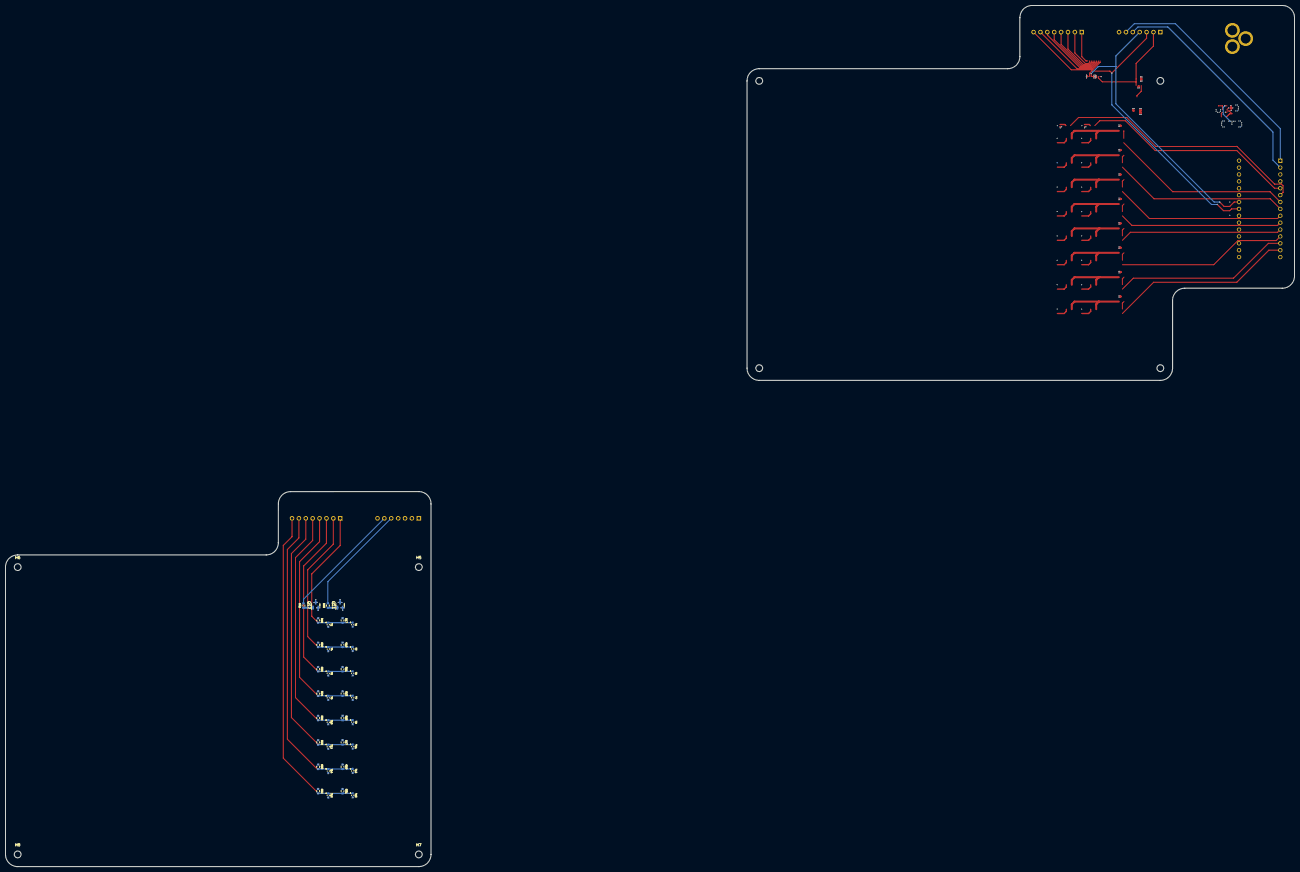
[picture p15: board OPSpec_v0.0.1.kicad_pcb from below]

Board: 4 copper layers, 475.6 x 317.7 mm, 115 parts (40 on the bottom side), 82 nets.

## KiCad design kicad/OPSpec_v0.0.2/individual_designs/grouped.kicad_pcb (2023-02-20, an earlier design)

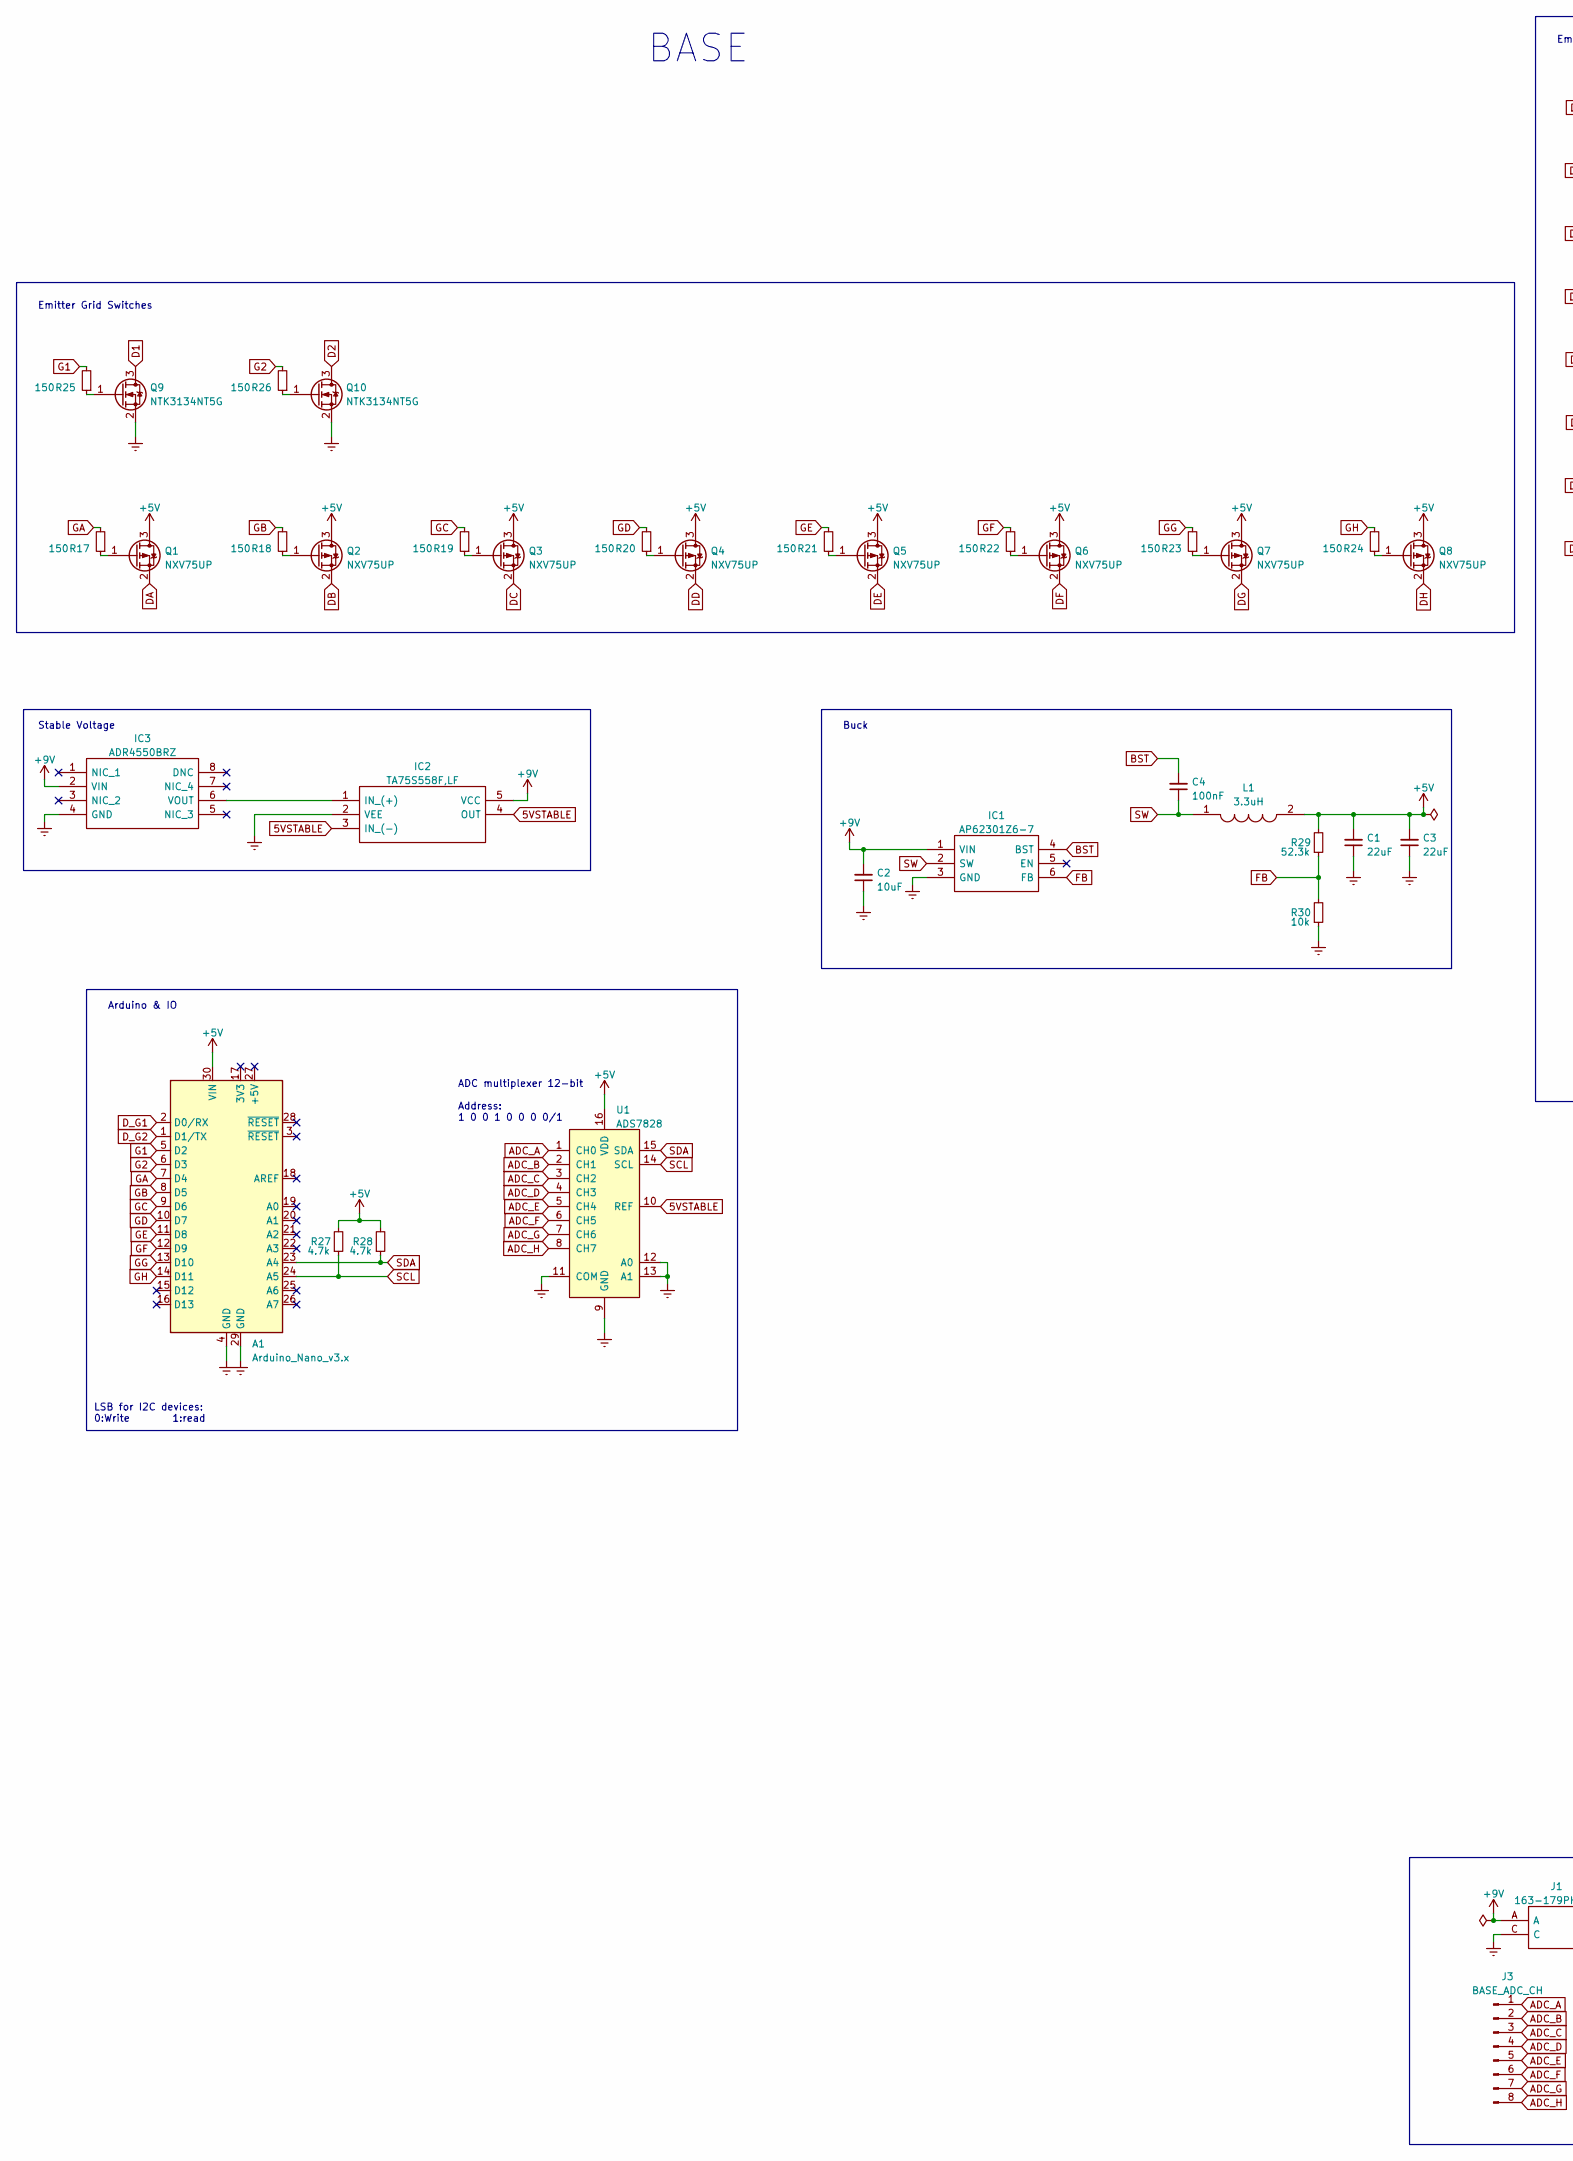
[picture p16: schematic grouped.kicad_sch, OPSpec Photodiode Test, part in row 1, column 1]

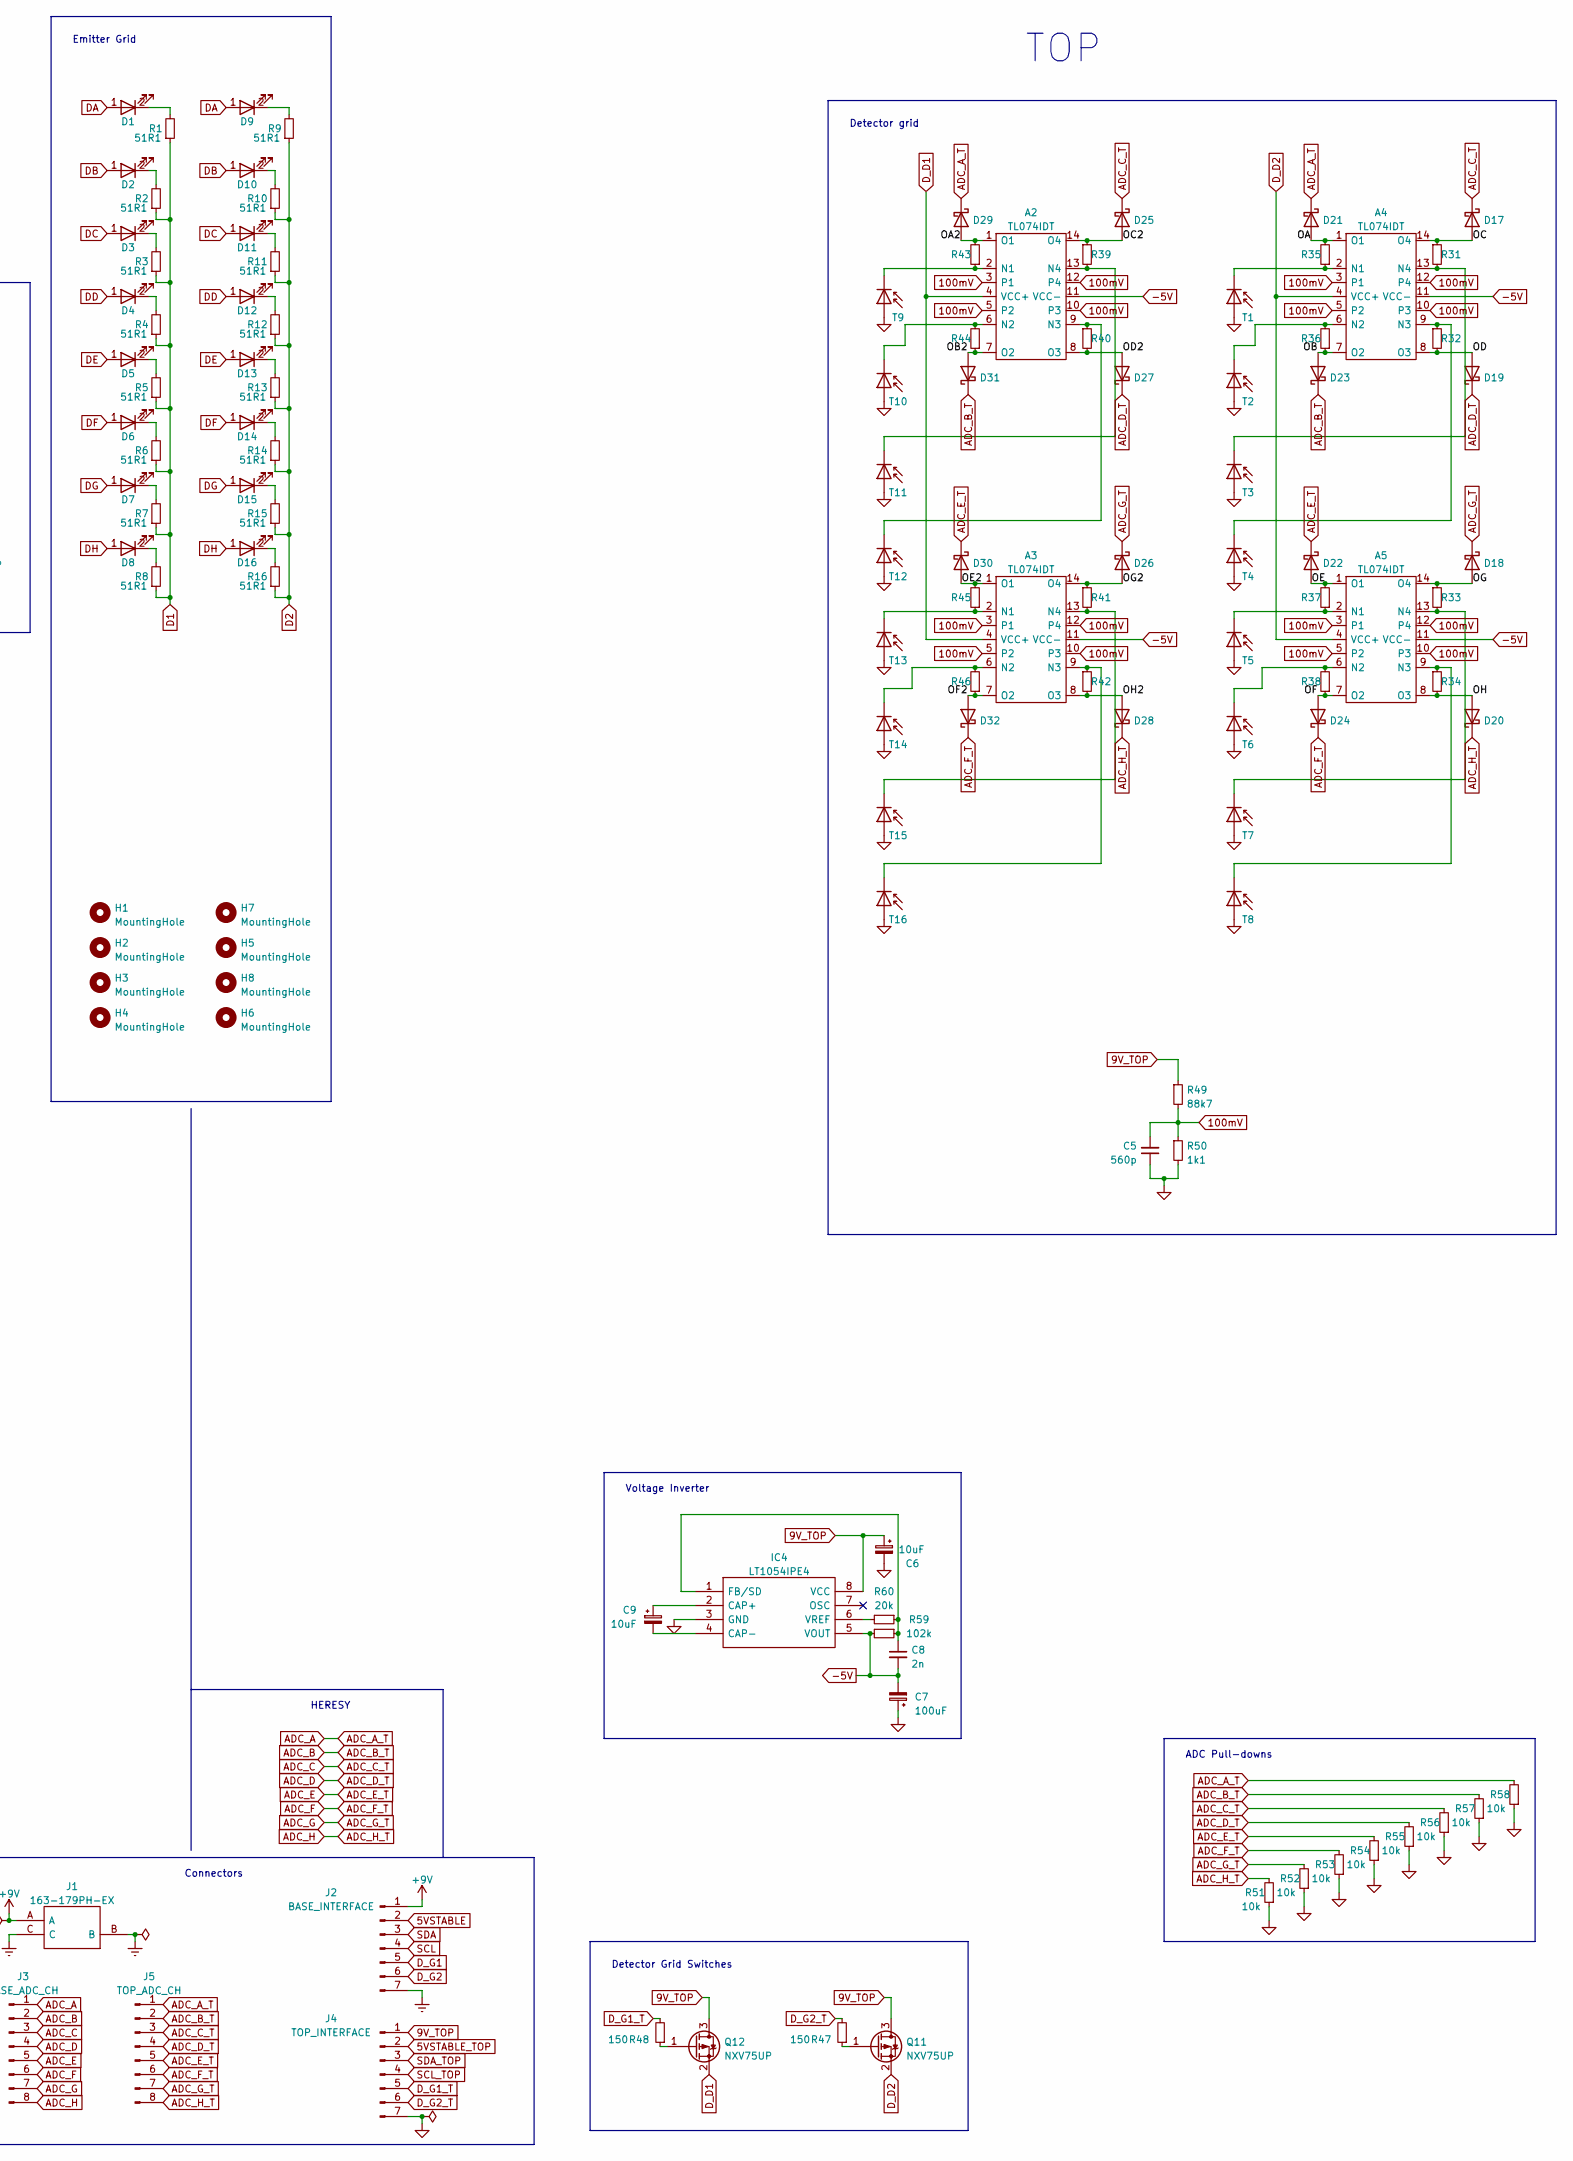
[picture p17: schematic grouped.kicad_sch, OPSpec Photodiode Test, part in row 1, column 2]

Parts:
A1: Arduino_Nano_v3.x; Arduino_Nano
A2, A3, A4, A5: TL074IDT; SOIC127P600X175-14N; Mouser Part Number 511-TL074IDT
C1, C3: 22uF; C_0805_2012Metric
C2: 10uF; C_0805_2012Metric
C4: 100nF; C_0805_2012Metric
C5: 560p; C_0805_2012Metric
C6, C9: 10uF; CP_EIA-3216-10_Kemet-I
C7: 100uF; CP_EIA-6032-15_Kemet-U
C8: 2n; C_0805_2012Metric
D1, D2, D3, D4, D5, D6, D7, D8, D9, D10, D11, D12, D13, D14, D15, D16: GR_JTLPS1.23-G7H4-45-1-150-R33; GRJTLPS123G7H4451150R33; Mouser Part Number 720-GRJTLPS123A1052
D17, D18, D19, D20, D21, D22, D23, D24, D25, D26, D27, D28, D29, D30, D31, D32: RB521S30T5G; SODFL1608X70N; Mouser Part Number 863-RB521S30T5G
H1, H2, H3, H4, H5, H6, H7, H8: MountingHole; MountingHole_2.5mm
IC1: AP62301Z6-7; SOTFL50P162X60-6N; Mouser Part Number 621-AP62301Z6-7
IC2: TA75S558F,LF; TA75S558FLF; Mouser Part Number 757-TA75S558FLF
IC3: ADR4550BRZ; SOIC127P600X175-8N; Mouser Part Number 584-ADR4550BRZ
IC4: LT1054IPE4; DIP794W53P254L959H508Q8N; Mouser Part Number 595-LT1054IPE4
J1: 163-179PH-EX; 163179PHEX; Mouser Part Number 163-179PH-EX
J2: BASE_INTERFACE; PinHeader_1x07_P2.54mm_Vertical
J3: BASE_ADC_CH; PinHeader_1x08_P2.54mm_Vertical
J4: TOP_INTERFACE; PinHeader_1x07_P2.54mm_Vertical
J5: TOP_ADC_CH; PinHeader_1x08_P2.54mm_Vertical
L1: 3.3uH; INDPM2016X100N; Mouser Part Number 963-MAKK2016T3R3M
Q1, Q2, Q3, Q4, Q5, Q6, Q7, Q8, Q11, Q12: NXV75UP; SOT-23
Q9, Q10: NTK3134NT5G; Mouser Part Number 863-NTK3134NT5G
R1, R2, R3, R4, R5, R6, R7, R8, R9, R10, R11, R12, R13, R14, R15, R16: 51R1; R_0603_1608Metric
R17, R18, R19, R20, R21, R22, R23, R24, R25, R26, R47, R48: 150; R_0603_1608Metric
R27, R28: 4.7k; R_0603_1608Metric
R29: 52.3k; R_0603_1608Metric
R30, R51, R52, R53, R54, R55, R56, R57, R58: 10k; R_0603_1608Metric
R31, R32, R33, R34, R35, R36, R37, R38, R39, R40, R41, R42, R43, R44, R45, R46: 2M55; R_0603_1608Metric
R49: 88k7; R_0603_1608Metric
R50: 1k1; R_0603_1608Metric
R59: 102k; R_0603_1608Metric
R60: 20k; R_0603_1608Metric
T1, T2, T3, T4, T5, T6, T7, T8, T9, T10, T11, T12, T13, T14, T15, T16: SFH2716 A01; SFH2716
U1: ADS7828; TSSOP-16_4.4x5mm_P0.65mm

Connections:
5VSTABLE: IC2.3 (IN_(-)), IC2.4 (OUT), J2.2, U1.10 (REF)
5VSTABLE_TOP: J4.2
9V_TOP: C6.1, IC4.8 (VCC), J4.1, Q11.3 (D), Q12.3 (D), R49.1
100mV: A2.3 (P1), A2.5 (P2), A2.10 (P3), A2.12 (P4), A3.3 (P1), A3.5 (P2), A3.10 (P3), A3.12 (P4), A4.3 (P1), A4.5 (P2), A4.10 (P3), A4.12 (P4), A5.3 (P1), A5.5 (P2), A5.10 (P3), A5.12 (P4), C5.2, R49.2, R50.1
+5V: A1.30 (VIN), C1.2, C3.2, L1.2, Q1.3 (D), Q2.3 (D), Q3.3 (D), Q4.3 (D), Q5.3 (D), Q6.3 (D), Q7.3 (D), Q8.3 (D), R27.2, R28.2, R29.2, U1.16 (VDD)
+9V: C2.2, IC1.1 (VIN), IC2.5 (VCC), IC3.2 (VIN), J1.A, J2.1
-5V: A2.11 (VCC-), A3.11 (VCC-), A4.11 (VCC-), A5.11 (VCC-), C7.2, C8.2, IC4.5 (VOUT), R59.2
/OA: A4.1 (O1), D21.2 (A), R35.2
/OA2: A2.1 (O1), D29.2 (A), R43.2
/OB: A4.7 (O2), D23.2 (A), R36.1
/OB2: A2.7 (O2), D31.2 (A), R44.1
/OC: A4.14 (O4), D17.2 (A), R31.1
/OC2: A2.14 (O4), D25.2 (A), R39.1
/OD: A4.8 (O3), D19.2 (A), R32.2
/OD2: A2.8 (O3), D27.2 (A), R40.2
/OE: A5.1 (O1), D22.2 (A), R37.2
/OE2: A3.1 (O1), D30.2 (A), R45.2
/OF: A5.7 (O2), D24.2 (A), R38.1
/OF2: A3.7 (O2), D32.2 (A), R46.1
/OG: A5.14 (O4), D18.2 (A), R33.1
/OG2: A3.14 (O4), D26.2 (A), R41.1
/OH: A5.8 (O3), D20.2 (A), R34.2
/OH2: A3.8 (O3), D28.2 (A), R42.2
ADC_A: D21.1 (K), D29.1 (K), J3.1, J5.1, R58.2, U1.1 (CH0)
ADC_B: D23.1 (K), D31.1 (K), J3.2, J5.2, R57.2, U1.2 (CH1)
ADC_C: D17.1 (K), D25.1 (K), J3.3, J5.3, R56.2, U1.3 (CH2)
ADC_D: D19.1 (K), D27.1 (K), J3.4, J5.4, R55.2, U1.4 (CH3)
ADC_E: D22.1 (K), D30.1 (K), J3.5, J5.5, R54.2, U1.5 (CH4)
ADC_F: D24.1 (K), D32.1 (K), J3.6, J5.6, R53.2, U1.6 (CH5)
ADC_G: D18.1 (K), D26.1 (K), J3.7, J5.7, R52.2, U1.7 (CH6)
ADC_H: D20.1 (K), D28.1 (K), J3.8, J5.8, R51.2, U1.8 (CH7)
BST: C4.2, IC1.4 (BST)
D1: Q9.3 (D), R1.1, R2.1, R3.1, R4.1, R5.1, R6.1, R7.1, R8.1
D2: Q10.3 (D), R9.1, R10.1, R11.1, R12.1, R13.1, R14.1, R15.1, R16.1
DA: D1.1 (A), D9.1 (A), Q1.2 (S)
DB: D2.1 (A), D10.1 (A), Q2.2 (S)
DC: D3.1 (A), D11.1 (A), Q3.2 (S)
DD: D4.1 (A), D12.1 (A), Q4.2 (S)
DE: D5.1 (A), D13.1 (A), Q5.2 (S)
DF: D6.1 (A), D14.1 (A), Q6.2 (S)
DG: D7.1 (A), D15.1 (A), Q7.2 (S)
DH: D8.1 (A), D16.1 (A), Q8.2 (S)
D_D1: A2.4 (VCC+), A3.4 (VCC+), Q12.2 (S)
D_D2: A4.4 (VCC+), A5.4 (VCC+), Q11.2 (S)
D_G1: A1.2 (D0/RX), J2.5
D_G1_T: J4.5, R48.2
D_G2: A1.1 (D1/TX), J2.6
D_G2_T: J4.6, R47.2
Earth: A1.4 (GND), A1.29 (GND), C1.1, C2.1, C3.1, IC1.3 (GND), IC2.2 (VEE), IC3.4 (GND), J1.B, J1.C, J2.7, Q9.2 (S), Q10.2 (S), R30.1, U1.9 (GND), U1.11 (COM), U1.12 (A0), U1.13 (A1)
FB: IC1.6 (FB), R29.1, R30.2
G1: A1.5 (D2), R25.2
G2: A1.6 (D3), R26.2
GA: A1.7 (D4), R17.2
GB: A1.8 (D5), R18.2
GC: A1.9 (D6), R19.2
GD: A1.10 (D7), R20.2
GE: A1.11 (D8), R21.2
GF: A1.12 (D9), R22.2
GG: A1.13 (D10), R23.2
GH: A1.14 (D11), R24.2
GND: C5.1, C6.2, C7.1, IC4.3 (GND), J4.7, R50.2, R51.1, R52.1, R53.1, R54.1, R55.1, R56.1, R57.1, R58.1, T1.1 (A), T2.1 (A), T3.1 (A), T4.1 (A), T5.1 (A), T6.1 (A), T7.1 (A), T8.1 (A), T9.1 (A), T10.1 (A), T11.1 (A), T12.1 (A), T13.1 (A), T14.1 (A), T15.1 (A), T16.1 (A)
unnamed: A2.2 (N1), R43.1, T9.2 (K)
unnamed: A2.6 (N2), R44.2, T10.2 (K)
unnamed: A2.9 (N3), R40.1, T12.2 (K)
unnamed: A2.13 (N4), R39.2, T11.2 (K)
unnamed: A3.2 (N1), R45.1, T13.2 (K)
unnamed: A3.6 (N2), R46.2, T14.2 (K)
unnamed: A3.9 (N3), R42.1, T16.2 (K)
unnamed: A3.13 (N4), R41.2, T15.2 (K)
unnamed: A4.2 (N1), R35.1, T1.2 (K)
unnamed: A4.6 (N2), R36.2, T2.2 (K)
unnamed: A4.9 (N3), R32.1, T4.2 (K)
unnamed: A4.13 (N4), R31.2, T3.2 (K)
unnamed: A5.2 (N1), R37.1, T5.2 (K)
unnamed: A5.6 (N2), R38.2, T6.2 (K)
unnamed: A5.9 (N3), R34.1, T8.2 (K)
unnamed: A5.13 (N4), R33.2, T7.2 (K)
unnamed: C8.1, IC4.1 (FB/SD), R59.1, R60.1
unnamed: C9.1, IC4.2 (CAP+)
unnamed: C9.2, IC4.4 (CAP-)
unnamed: D1.2 (K), R1.2
unnamed: D2.2 (K), R2.2
unnamed: D3.2 (K), R3.2
unnamed: D4.2 (K), R4.2
unnamed: D5.2 (K), R5.2
unnamed: D6.2 (K), R6.2
unnamed: D7.2 (K), R7.2
unnamed: D8.2 (K), R8.2
unnamed: D9.2 (K), R9.2
unnamed: D10.2 (K), R10.2
unnamed: D11.2 (K), R11.2
unnamed: D12.2 (K), R12.2
unnamed: D13.2 (K), R13.2
unnamed: D14.2 (K), R14.2
unnamed: D15.2 (K), R15.2
unnamed: D16.2 (K), R16.2
unnamed: IC2.1 (IN_(+)), IC3.6 (VOUT)
unnamed: IC4.6 (VREF), R60.2
unnamed: Q1.1 (G), R17.1
unnamed: Q2.1 (G), R18.1
unnamed: Q3.1 (G), R19.1
unnamed: Q4.1 (G), R20.1
unnamed: Q5.1 (G), R21.1
unnamed: Q6.1 (G), R22.1
unnamed: Q7.1 (G), R23.1
unnamed: Q8.1 (G), R24.1
unnamed: Q9.1 (G), R25.1
unnamed: Q10.1 (G), R26.1
unnamed: Q11.1 (G), R47.1
unnamed: Q12.1 (G), R48.1
SCL: A1.24 (A5), J2.4, R27.1, U1.14 (SCL)
SCL_TOP: J4.4
SDA: A1.23 (A4), J2.3, R28.1, U1.15 (SDA)
SDA_TOP: J4.3
SW: C4.1, IC1.2 (SW), L1.1

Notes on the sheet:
ADC multiplexer 12-bit Address: 1 0 0 1 0 0 0 0/1
Arduino & IO
HERESY
Connectors
ADC Pull-downs
Detector Grid Switches
Emitter Grid Switches
Detector grid
TOP
BASE
Buck
Voltage Inverter
LSB for I2C devices: 0:Write 1:read
Emitter Grid
Stable Voltage

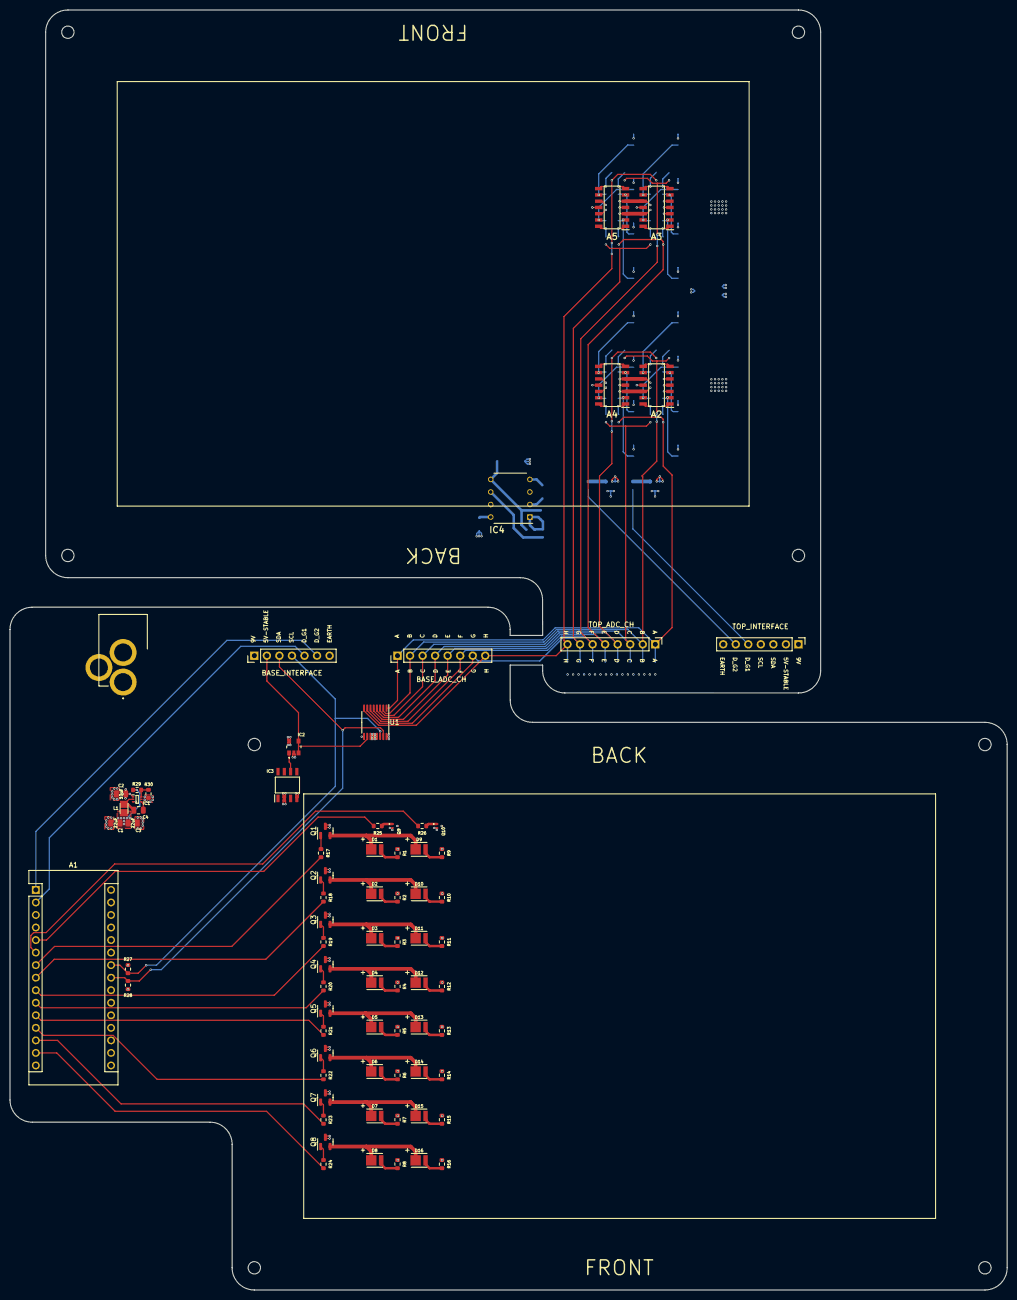
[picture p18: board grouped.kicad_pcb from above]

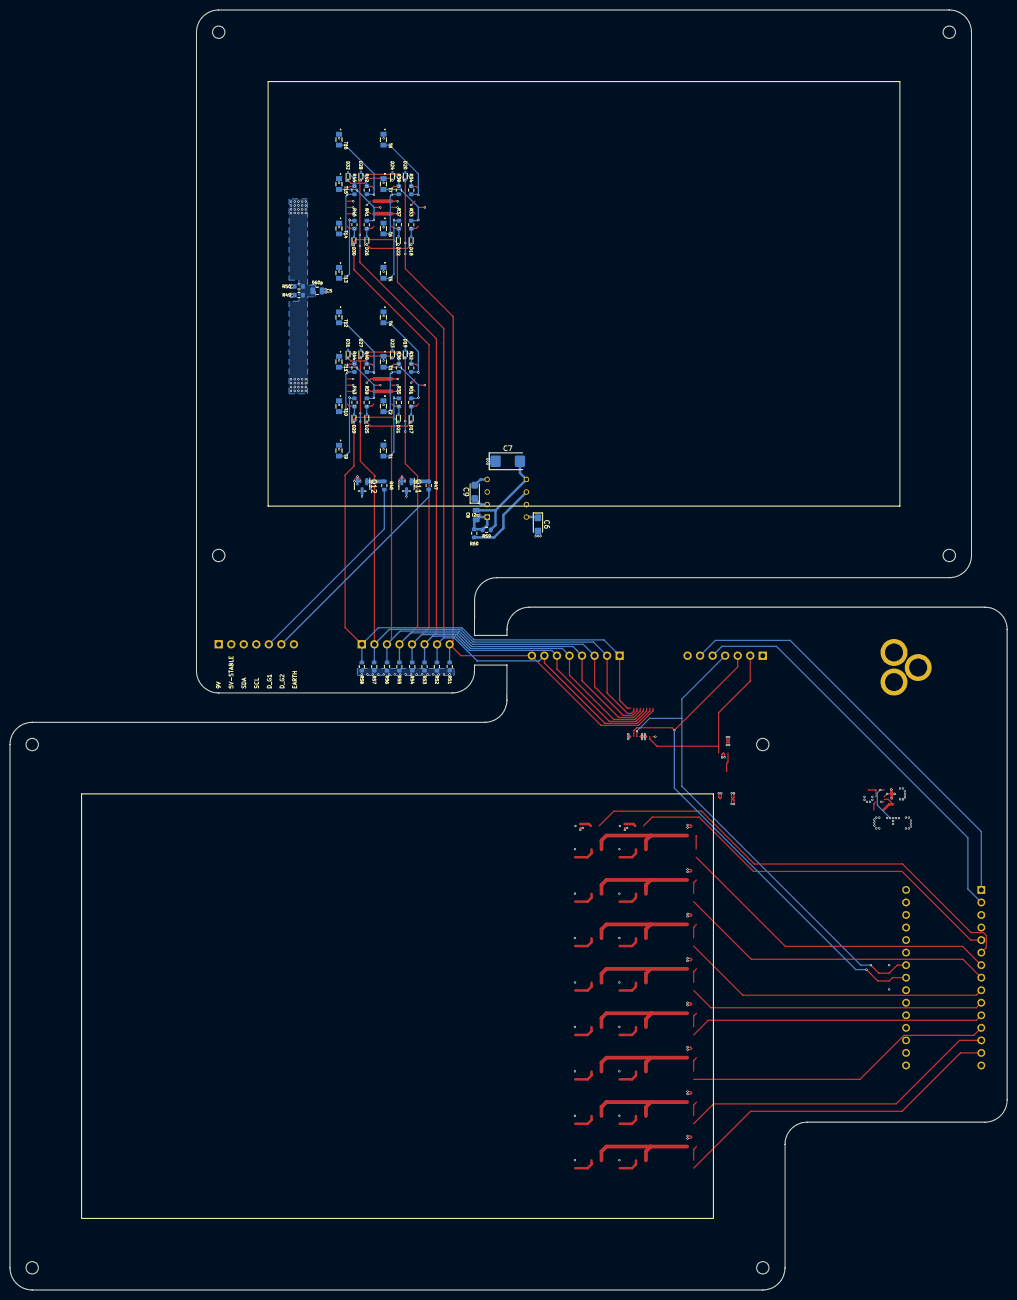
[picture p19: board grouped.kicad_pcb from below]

Board: 4 copper layers, 202.0 x 259.3 mm, 153 parts (73 on the bottom side), 112 nets.

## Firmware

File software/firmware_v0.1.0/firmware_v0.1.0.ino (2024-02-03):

/**
 * @file firmware_v0.1.0.ino
 * @author Sachit Kshatriya
 * @brief Interface firmware for the 96-well OPSpec
 * @version 0.1
 * @date 2022-11-27
 *
 */

#include <Wire.h>

// ALWAYS GIVE I2C 7-BIT ADDRESSES FUUUUUUUUUUUUUUCK
// I2C devices
#define ADC 0b1001000
#define EROW 0b0100001 // p-ch
#define ECOL 0b0100000 // n-ch
#define DCOL 0b0100011 // p-ch

// I/O expander registers
#define IN0 0x00 // input read
#define IN1 0x01
#define OUT0 0x02 // output set
#define OUT1 0x03
#define INV0 0x04 // polarity inversion
#define INV1 0x05
#define CONFIG0 0x06 // configuration
#define CONFIG1 0x07

// additional parameters
int ledOn = 5;   // in ms
int deadTime = 1; // in ms - time between actions on different functional units

// The ADC channel addresses in single-ended input mode arranged by index (A - H)
byte chAddr[8] = {0b1000, 0b1100, 0b1001, 0b1101,
                  0b1010, 0b1110, 0b1011, 0b1111};

// Converstion buffer for transmission over Serial
unsigned int raw[12][8];

bool oneloop;

void setup()
{
    Serial.begin(115200);

    Wire.begin();
    delay(500);

    // Set I/O expander pins to keep grids inactive on startup
    // Unconnected pins set to high-Z input mode
    commandIO(ECOL, OUT0, 0x00, 0x00);    // output low for n-ch
    commandIO(ECOL, CONFIG0, 0x00, 0xF0); // pin config to output (1 = highZ-in)

    commandIO(EROW, OUT0, 255, 255);  // output high for p-ch
    commandIO(EROW, CONFIG0, 0, 255); // pin config to output

    commandIO(DCOL, OUT0, 255, 255);         // output high for p-ch
    commandIO(DCOL, CONFIG0, 0, 0b11110000); // pin config to output

    oneloop = true;

    delay(50);
}

void loop()
{
    handleSerial();
}

/**
 * @brief Handles execution control over Serial
 *
 */
void handleSerial()
{

    while (Serial.available() > 0)
    {
        char incomingCharacter = Serial.read();
        switch (incomingCharacter)
        {
        case '0':
            flushRaw();
            readDark();
            sendRaw();
            Serial.flush();
            break;

        case 'A':
            flushRaw(); 
            readSamples();
            sendRaw();
            break;

        case 'T':
            blinkLEDs(20);
            break;
        }
    }
}

/**
 * @brief Reads raw ADC conversions into the buffer without turning on LEDs
 *
 */
void readDark()
{

    for (int i = 0; i < 12; i++) // col loop
    {
        addressDetCol(i, 1); // enable detector column

        delay(10);

        for (int j = 0; j < 8; j++) // row loop
        {
            delay(ledOn); // let reading settle

            readADCValue(chAddr[j], raw[i], j);

            delay(deadTime);

            // for debugging
            // Serial.print("raw[" + String(i) + "][" + j + "] is: ");
            // Serial.println(raw[i][j]);
        }
    }
    addressDetCol(11, 0); // disable detector column at the end
}

/**
 * @brief Reads raw ADC conversions for well samples into the buffer
 *
 */
void readSamples()
{

    for (int i = 0; i < 12; i++) // col loop
    {

        addressDetCol(i, 1); // det col on
        delay(10);

        for (int j = 0; j < 8; j++) // row loop
        {
            addressLED(i, j, 1); // LED on
            delay(ledOn);        // let LED settle

            readADCValue(chAddr[j], raw[i], j);

            delay(deadTime);

            // for debugging
            // Serial.print("raw[" + String(i) + "][" + j + "] is: ");
            // Serial.println(raw[i][j]);
        }
    }

    addressDetCol(0, 0); // all detectors off
    addressLED(0, 0, 0); // all LEDs off
}

/**
 * @brief Reads ADC conversion for a well and prints to Serial
 *
 * @param col well column index
 * @param row  well row index
 */
void readWell(int col, int row)
{

    addressDetCol(col, 1); // det col on
    delay(10);

    addressLED(col, row, 1); // LED on
    delay(ledOn);

    readADCValue(chAddr[row], raw[col], row);

    // for debugging
    // Serial.print("raw[" + String(col) + "][" + row + "] is: ");
    // Serial.println(raw[col][row], DEC);

    // reset LEDs and detector switches to off state
    addressDetCol(0, 0); // all detectors off
    addressLED(0, 0, 0); // all LEDs off
}

/**
 * @brief Flushes the conversion data buffer with -1
 *
 */
void flushRaw()
{
    for (int i = 0; i < 12; i++)
    {
        for (int j = 0; j < 8; j++)
        {
            raw[i][j] = -1;
        }
    }
}

/**
 * @brief Writes contents of the conversion data buffer to serial. Flattens data into groups of columns.
 * Element 0 is well[col][row] = well[0][0], element 1 is well[0][1].
 *
 */
void sendRaw()
{
    for (int i = 0; i < 12; i++) // column loop
    {
        for (int j = 0; j < 8; j++) // row loop
        {
            Serial.println(raw[i][j]);
        }
    }
}

/**
 * @brief Commands a conversion and reads the value for the given
 * ADC channel into the array at the given index after concatenating into an int
 *
 * @param channel ADC channel to read from. 4-bit value address stored in a byte.
 * @param convData pointer to store conversion data
 * @param idx index at which to store the data
 * @return int
 */
int readADCValue(byte channel, unsigned int *convData, int idx)
{

    byte commandByte = (channel << 4) + 0b1100; // internal ref on and ADC conv ON

    Wire.beginTransmission(ADC);
    Wire.write(commandByte);
    Wire.endTransmission();

    delay(1); // let the ADC settle idk

    Wire.requestFrom(ADC, 2);

    // Get and store the conversion
    int temp = Wire.read();
    int t2 = Wire.read();

    int tot = (temp << 8) + t2;
    convData[idx] = tot;
}

/**
 * @brief Wrapper function to address individual LEDs in the emitter grid
 *
 * @param col LED column id - left to right
 * @param row LED row id - top to bottom
 * @param action 0 for OFF; 1 for ON
 */
void addressLED(int col, int row, bool action)
{
    byte colPorts[2] = {0, 0};       // default to off
    byte rowPorts[2] = {0xFF, 0xFF}; // default to off

    if (action)
    {
        bitSet(colPorts[int(col / 8)], col % 8);   // turn col on
        bitClear(rowPorts[int(row / 8)], row % 8); // turn row on
    }

    // send port values to the devices
    commandIO(ECOL, OUT0, colPorts[0], colPorts[1]);
    commandIO(EROW, OUT0, rowPorts[0], rowPorts[1]);
}

/**
 * @brief Addresses photodiode column FETs for power delivery
 *
 * @param col photodiode column id - T1:column 0
 * @param action 0 for OFF; 1 for ON
 */
void addressDetCol(int col, bool action)
{
    byte colPorts[2] = {0xFF, 0xFF}; // default to off

    if (action)
        bitClear(colPorts[int(col / 8)], col % 8); // turn col on

    commandIO(DCOL, OUT0, colPorts[0], colPorts[1]);
}

/**
 * @brief Sets a register pair for the given I/O expander
 *
 * @param device I2C address
 * @param port0Reg command byte to port0 of a register pair
 * @param port0 port0 data
 * @param port1 port1 data
 */
void commandIO(byte device, byte port0Reg, byte port0, byte port1)
{
    Wire.beginTransmission(device);

    // send command byte to write to port0 registers
    Wire.write(port0Reg);

    // since port0 element of the register pair is
    // accessed first the data write can be sequential
    Wire.write(port0);
    Wire.write(port1);

    Wire.endTransmission();
    // Serial.println(Wire.endTransmission());
}

/**
 * @brief Cycles through all the LEDs
 * @param msPerLed How long to keep an LED turned on in ms
 */
void blinkLEDs(int msPerled)
{
    for (int i = 0; i < 12; i++)
    {
        for (int j = 0; j < 8; j++)
        {
            addressLED(i, j, 1);
            delay(msPerled);
        }
    }

    addressLED(0, 0, 0);
}

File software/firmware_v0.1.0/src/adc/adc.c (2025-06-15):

/**
 * @file adc.c
 * @author Sachit Kshatriya
 * @brief Functions for the ADC
 * @version 0.1.0
 * @date 2025-06-14
 *
 */

#include <stdint.h>
#include <Wire.h>

#include "adc.h"
#include "../det_grid/detectors.h"

#define I2C_ADC 0b1001000

// The ADC channel addresses in single-ended input mode arranged by index (A - H)
static uint8_t chAddr[8] = {0b1000, 0b1100, 0b1001, 0b1101,
                            0b1010, 0b1110, 0b1011, 0b1111};

static uint16_t read;

uint16_t read_well_value(int col, int row)
{
    enable_det(col);

    byte commandByte = (chAddr[row] << 4) + 0b1100; // internal ref on and ADC conv ON

    Wire.beginTransmission(I2C_ADC);
    Wire.write(commandByte);
    Wire.endTransmission();

    Wire.requestFrom(I2C_ADC, 2);

    // Get and store the conversion
    uint16_t temp = Wire.read();
    uint16_t t2 = Wire.read();

    uint16_t tot = (temp << 8) + t2;
    return tot;
}

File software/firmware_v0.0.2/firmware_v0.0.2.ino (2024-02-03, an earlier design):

/**
 * @file firmware_v0.0.2.ino
 * @author Sachit Kshatriya
 * @brief Interface firmware for the OPSpec linear test
 * @version 0.1
 * @date 2022-07-17
 *
 */

#include <Wire.h>

// ADC address
#define ADC 0b1001000

// Define the LED grid control gate pins
// p-ch
int DetOne = 0;
int DetTwo = 1;

// n-ch
int one = 2;
int two = 3;

// p-ch
int A = 4;
int B = 5;
int C = 6;
int D = 7;
int E = 8;
int F = 9;
int G = 10;
int H = 11;

// additional parameters
int ledOn = 50;  // in ms
int deadTime = 1; // in ms - time between actions on different functional units

// The ADC channel addresses in single-ended input mode arranged by index (A - H)
byte chAddr[8] = {0b1000, 0b1100, 0b1001, 0b1101,
                  0b1010, 0b1110, 0b1011, 0b1111};

bool oneLoop;

void setup()
{

    Serial.begin(115200);

    Wire.begin();

    // Set pin modes to output:
    for (int i = 0; i < 12; i++)
    {
        pinMode(i, OUTPUT);
    }

    // Turn n-FETs off
    digitalWrite(2, LOW);
    digitalWrite(3, LOW);

    // Turn p-FETs off
    digitalWrite(0, HIGH);
    digitalWrite(1, HIGH);
    digitalWrite(4, HIGH);
    digitalWrite(5, HIGH);
    digitalWrite(6, HIGH);
    digitalWrite(7, HIGH);
    digitalWrite(8, HIGH);
    digitalWrite(9, HIGH);
    digitalWrite(10, HIGH);
    digitalWrite(11, HIGH);

    oneLoop = true;
}

int raw[2][8];

void loop()
{

    handleSerial();

    // delay(500); // allow serial monitor to open

    // Serial.println();
    // Serial.println();
    // readADCs();
    // readDet();
    // sendRaw();

    // flushRaw();
    // sendRaw();

    // oneLoop = false;

    // blinkLEDs();
}

int readADCValue(byte channel, int *convData, int idx)
{
    /**
     * @brief Commands a conversion and reads the value for the given
     * ADC channel into the array at the given index after concatenating into an int
     */

    byte commandByte = (channel << 4) + 0b0100; // internal ref off and ADC conv ON

    Wire.beginTransmission(ADC);
    Wire.write(commandByte);
    Wire.endTransmission();

    delay(5); // maybe let the ADC settle idk

    Wire.requestFrom(ADC, 2);

    // Get and store the conversion
    int temp = Wire.read() << 8;
    temp += Wire.read();

    convData[idx] = temp;
    // convData[1] = Wire.read();
}

void blinkLEDs()
{
    /**
     * @brief Tests the LED array by cycling through them
     *
     */

    int rows[] = {A, B, C, D, E, F, G, H};
    int cols[] = {one, two};

    for (int i = 0; i < 2; i++)
    {
        digitalWrite(cols[i], HIGH);

        for (int j = 0; j < 8; j++)
        {
            digitalWrite(rows[j], LOW);
            delay(200);
            digitalWrite(rows[j], HIGH);
        }

        digitalWrite(cols[i], LOW);
    }
}

void readADCs()
{
    /**
     * @brief Returns raw ADC conversions for each well
     *
     */

    int rows[] = {A, B, C, D, E, F, G, H};
    int cols[] = {one, two};
    int detCols[] = {DetOne, DetTwo};

    for (int i = 0; i < 2; i++) // col loop
    {
        digitalWrite(cols[i], HIGH);   // LED col on
        digitalWrite(detCols[i], LOW); // det col on

        delay(10);

        for (int j = 0; j < 8; j++) // row loop
        {
            digitalWrite(rows[j], LOW); // LED row on
            delay(ledOn);               // let reading settle

            readADCValue(chAddr[j], raw[i], j);

            delay(deadTime);

            // for debugging
            // Serial.print("raw[" + String(i) + "][" + j + "] is: ");
            // Serial.println(raw[i][j]);

            digitalWrite(rows[j], HIGH); // LED row off
        }

        digitalWrite(cols[i], LOW);     // LED col off
        digitalWrite(detCols[i], HIGH); // det col off
    }
}

void flushRaw()
{
    /**
     * @brief Flushes the conversion data buffer with -1s
     */

    for (int i = 0; i < 2; i++)
    {
        for (int j = 0; j < 8; j++)
        {
            raw[i][j] = -1;
        }
    }
}

void sendRaw()
{
    /**
     * @brief Writes contents of the conversion data buffer to serial
     */

    for (int i = 0; i < 2; i++)
    {
        for (int j = 0; j < 8; j++)
        {
            Serial.println(raw[i][j]);
        }
    }
}

void handleSerial()
{
    /**
     * @brief Handles execution control over Serial
     */

    while (Serial.available() > 0)
    {
        char incomingCharacter = Serial.read();
        switch (incomingCharacter)
        {
        case '0':
            readDet();
            // sendRaw();

        case 'A':
            readADCs();
            sendRaw();
        }
    }
}

void readDet()
{
    /**
     * @brief Reads the ADC outputs into the buffer with no LED activation
     */
    int rows[] = {A, B, C, D, E, F, G, H};
    int cols[] = {one, two};
    int detCols[] = {DetOne, DetTwo};

    for (int i = 0; i < 2; i++) // col loop
    {
        digitalWrite(detCols[i], LOW); // det col on

        delay(10);

        for (int j = 0; j < 8; j++) // row loop
        {
            delay(ledOn); // let reading settle

            readADCValue(chAddr[j], raw[i], j);

            delay(deadTime);

            // for debugging
            // Serial.print("raw[" + String(i) + "][" + j + "] is: ");
            // Serial.println(raw[i][j]);
        }

        digitalWrite(detCols[i], HIGH); // det col off
    }
}

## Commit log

2024-02-03 Prep cleanup
    [OPSpec_v0.1.0.kicad_sch, housing.FCStd]
2025-06-15 Routine kicad save update
    [OPSpec_v0.1.0.kicad_sch]
2025-06-15 Led interafacing functions
